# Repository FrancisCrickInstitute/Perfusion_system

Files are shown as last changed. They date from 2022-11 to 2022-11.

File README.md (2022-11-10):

# Perfusion_system

This system is composed by a 3D printed lid for 35 mm petri dishes, two peristaltic pumps and a control board which controls the flow rate of both pumps simultaneously.



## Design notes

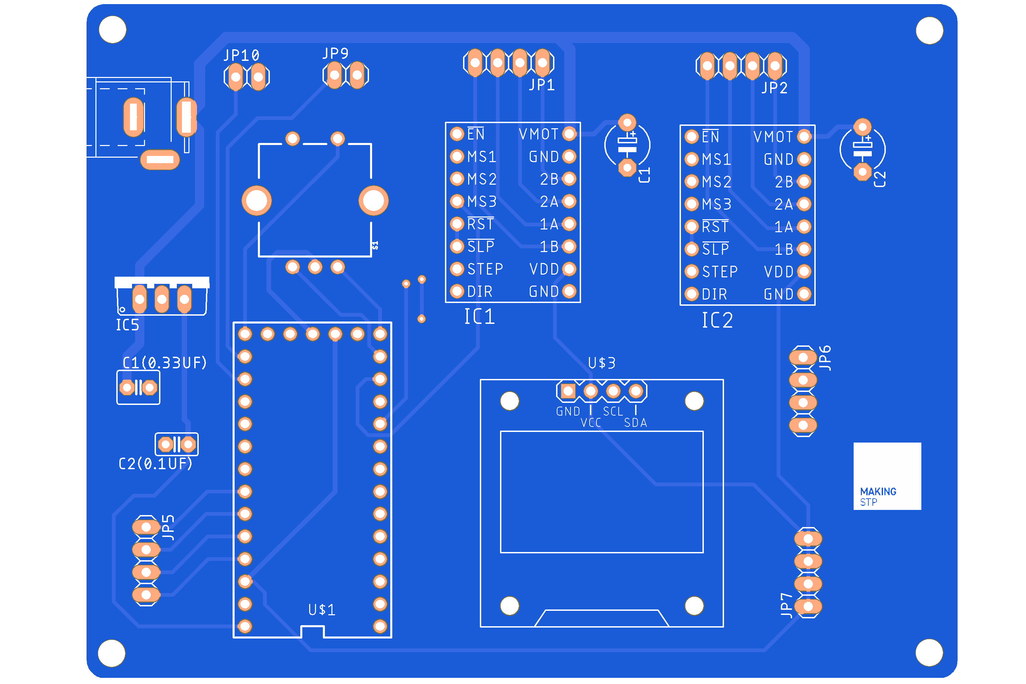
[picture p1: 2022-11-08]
Design files/Electronics/2 stepper board.png

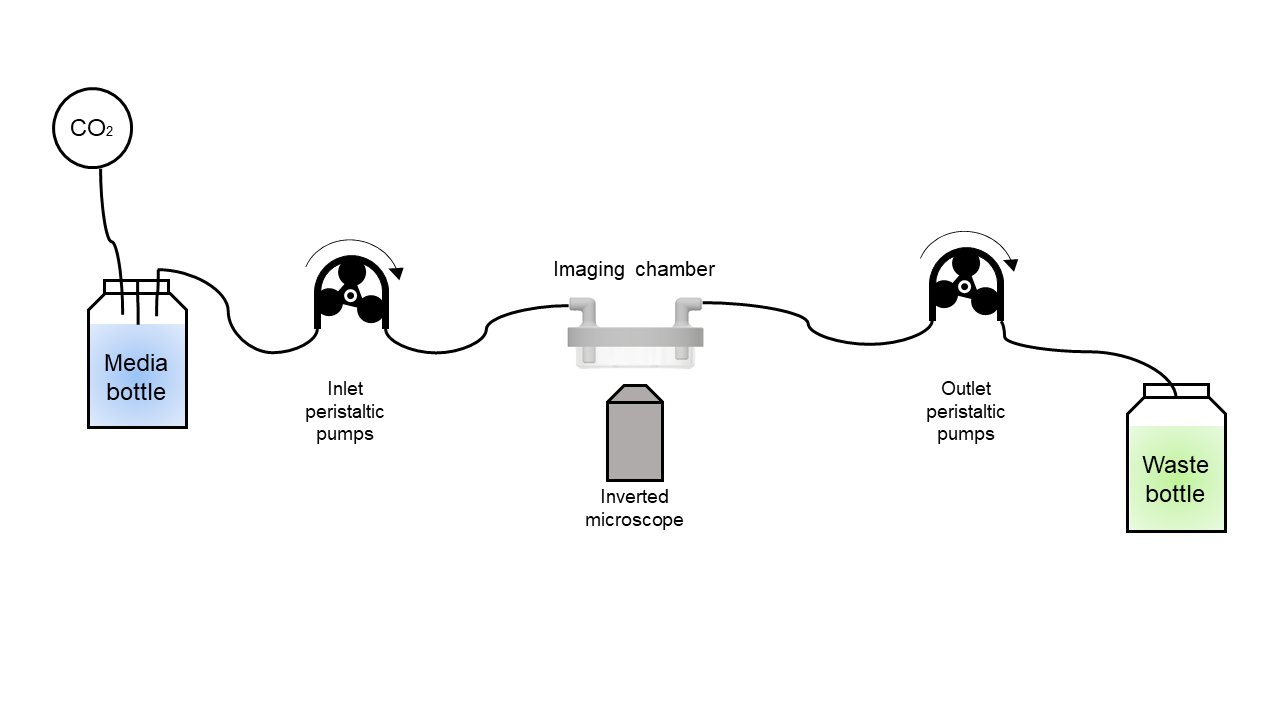
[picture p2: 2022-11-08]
Perfusion system.png

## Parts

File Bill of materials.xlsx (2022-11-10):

Component | Units | Manufacturer Hyperlink embedded) | Unit cost £ | Cost £
Peristaltic pumps | 2 | Amazon (https://www.amazon.co.uk/Elprico-Peristaltic-Pump-12-24V-Micro/dp/B08TLVLJKD) | 36.00 | 72.00
Silicone tubing 2mm ID/ 4mm OD | 1 | RS Components (https://uk.rs-online.com/web/p/flexible-tubes/4189999/)
Teensy 3.2 | 1 | Amazon (https://www.amazon.co.uk/Teensy-3-2-With-Pins/dp/B015QUPO5Y) | 22.39 | 22.39
Barrel jack | 1 | Amazon (https://www.amazon.co.uk/Bottam-Power-Socket-2-1mm-Barrel-Type/dp/B09MQTLXJK?spLa=ZW5jcnlwdGVkUXVhbGlmaWVyPUExMFMxMU8wNUpKUVJ) | 0.10 | 0.10
OLED display | 1 | Amazon (https://www.amazon.co.uk/gp/product/B01L9GC470/ref=ppx_yo_dt_b_search_asin_title?ie=UTF8&th=1) | 5.99 | 5.99
2.54 mm Female pin header | 2 | Amazon (https://www.amazon.co.uk/HALJIA-Header-Connector-2-54mm-StripWires/dp/B06WD34L1H) | 0.50 | 1.00
Screw connectors | 4 | Amazon (https://www.amazon.co.uk/UCTOP-STORE-2-54mm-Terminal-Connector/dp/B01FS4KDN6) | 0.33 | 1.33
Pololu A4988 Stepper Motor Driver Carrier | 2 | Pimoroni (https://shop.pimoroni.com/products/pololu-a4988-stepper-motor-driver-carrier-black-edition?variant=385708716&currency=GBP) | 7.50 | 15.00
5V 1.5A Linear Voltage Regulator - 7805 | 1 | ThePiHut (https://thepihut.com/products/5v-1-5a-linear-voltage-regulator-7805-to-220) | 0.80 | 0.80
330 nF ceramic capacitor | 1 | ThePiHut (https://thepihut.com/products/capacitor-0-33-f-10-pack) | 0.09 | 0.09
100 nF ceramic capacitor | 1 | ThePiHut (https://thepihut.com/products/0-1uf-ceramic-capacitors-10-pack) | 0.17 | 0.17
Rotary encoder | 1 | ThePiHut (https://thepihut.com/products/rotary-encoder-extras) | 3.90 | 3.90
PCB | 1 | Gerber file (JCB PCB) (https://cart.jlcpcb.com/quote?orderType=1&stencilLayer=2&stencilWidth=100&stencilLength=100) | 2.00 | 2.00
12V power supply Barrel jack 2.1mm | 1 | Amazon (https://www.amazon.co.uk/12V-3A-Adapter-Keyboard-Approved/dp/B0B8JX1MZ4) | 12.00 | 2.00
35 mm lid | 2 | 3D printed | 1.00 | 1.00
 |  |  | Total cost | 127.77

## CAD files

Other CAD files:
Design files/Ibidi 35 mm custom dish.ipt

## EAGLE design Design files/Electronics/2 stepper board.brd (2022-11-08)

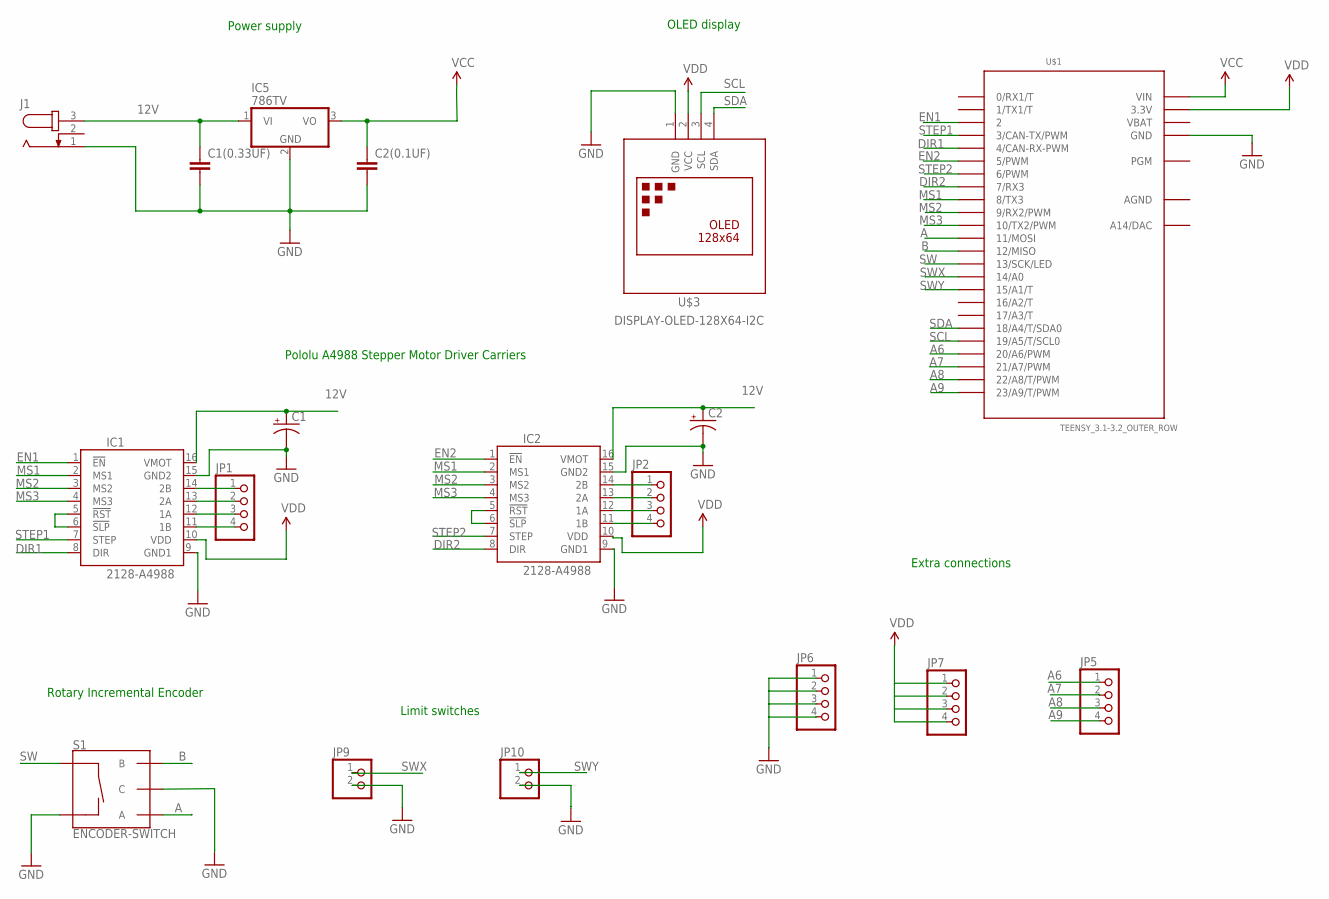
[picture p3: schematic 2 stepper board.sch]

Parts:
C1, C2: CPOL-USE5-5; E5-5
C1(0.33UF): C2.5/4; C2.5-4
C2(0.1UF): C2.5/2; C2.5-2
IC1, IC2: 2128-A4988; A4988
IC5: 786TV; TO220V
J1: JACK-PLUG0; SPC4077
JP1, JP2, JP5, JP6, JP7: PINHD-1X4; 1X04
JP9, JP10: PINHD-1X2; 1X02
S1: ENCODER-SWITCH; ROTARY_ENC_PLAIN
U$1: TEENSY_3.1-3.2_OUTER_ROW; TEENSY_3.0-3.2&LC_OUTER_ROW
U$3: DISPLAY-OLED-128X64-I2C

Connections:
12V: C1.+, C1(0.33UF).1, C2.+, IC1.16 (VMOT), IC2.16 (VMOT), IC5.1 (VI), J1.3
A: S1.A, U$1.11 (11/MOSI)
A6: JP5.1, U$1.20/A6 (20/A6/PWM)
A7: JP5.2, U$1.21/A7 (21/A7/PWM)
A8: JP5.3, U$1.22/A8 (22/A8/T/PWM)
A9: JP5.4, U$1.23/A9 (23/A9/T/PWM)
AGND: U$1.AGND
B: S1.B, U$1.12 (12/MISO)
DIR1: IC1.8 (DIR), U$1.4 (4/CAN-RX-PWM)
DIR2: IC2.8 (DIR), U$1.7 (7/RX3)
EN1: IC1.1 (!EN), U$1.2
EN2: IC2.1 (!EN), U$1.5 (5/PWM)
GND: C1.-, C1(0.33UF).2, C2.-, C2(0.1UF).2, IC1.9 (GND1), IC1.15 (GND2), IC2.9 (GND1), IC2.15 (GND2), IC5.2 (GND), J1.1, JP6.1, JP6.2, JP6.3, JP6.4, JP9.2, JP10.2, S1.C, S1.SW-, U$1.GND, U$1.GND1 (GND), U$3.1 (GND)
MS1: IC1.2 (MS1), IC2.2 (MS1), U$1.8 (8/TX3)
MS2: IC1.3 (MS2), IC2.3 (MS2), U$1.9 (9/RX2/PWM)
MS3: IC1.4 (MS3), IC2.4 (MS3), U$1.10 (10/TX2/PWM)
unnamed: IC1.14 (2B), JP1.1
unnamed: IC1.13 (2A), JP1.2
unnamed: IC1.12 (1A), JP1.3
unnamed: IC1.11 (1B), JP1.4
unnamed: IC2.14 (2B), JP2.1
unnamed: IC2.13 (2A), JP2.2
unnamed: IC2.12 (1A), JP2.3
unnamed: IC2.11 (1B), JP2.4
unnamed: IC2.5 (!RST), IC2.6 (!SLP)
unnamed: IC1.5 (!RST), IC1.6 (!SLP)
SCL: U$1.19/A5 (19/A5/T/SCL0), U$3.3 (SCL)
SDA: U$1.18/A4 (18/A4/T/SDA0), U$3.4 (SDA)
STEP1: IC1.7 (STEP), U$1.3 (3/CAN-TX/PWM)
STEP2: IC2.7 (STEP), U$1.6 (6/PWM)
SW: S1.SW+, U$1.13 (13/SCK/LED)
SWX: JP9.1, U$1.14/A0
SWY: JP10.1, U$1.15/A1 (15/A1/T)
VBAT: U$1.VBAT
VCC: C2(0.1UF).1, IC5.3 (VO), U$1.VIN
VDD: IC1.10 (VDD), IC2.10 (VDD), JP7.1, JP7.2, JP7.3, JP7.4, U$1.3.3V, U$1.3.3V1 (3.3V), U$3.2 (VCC)

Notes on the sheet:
Pololu A4988 Stepper Motor Driver Carriers
OLED display
Power supply
Rotary Incremental Encoder
Extra connections
Limit switches

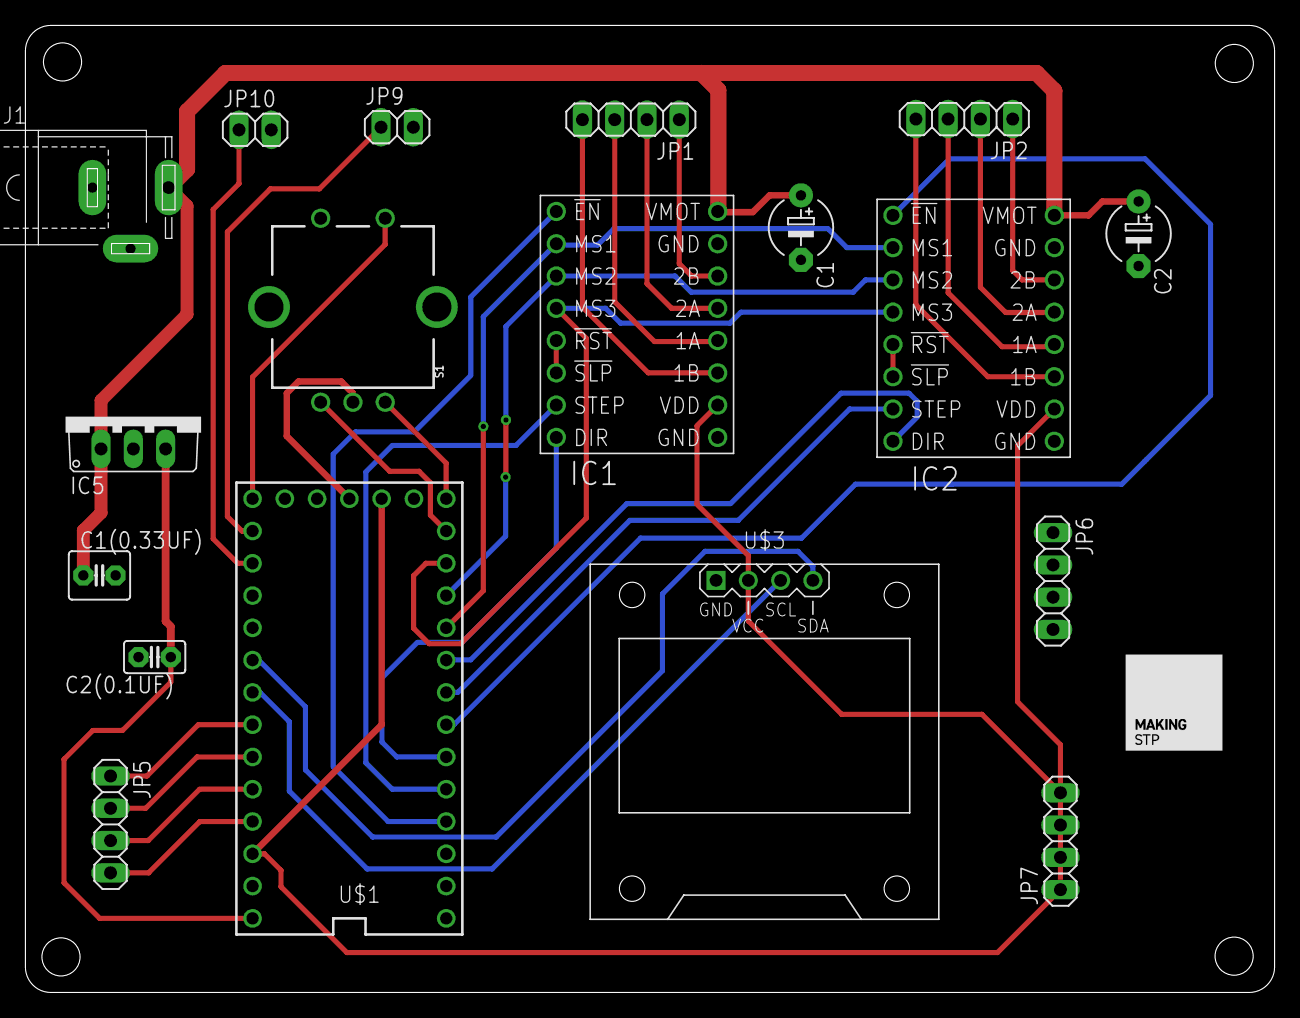
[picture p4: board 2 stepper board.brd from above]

Board: 2 copper layers, 98.3 x 76.1 mm, 18 parts (0 on the bottom side), 34 nets.

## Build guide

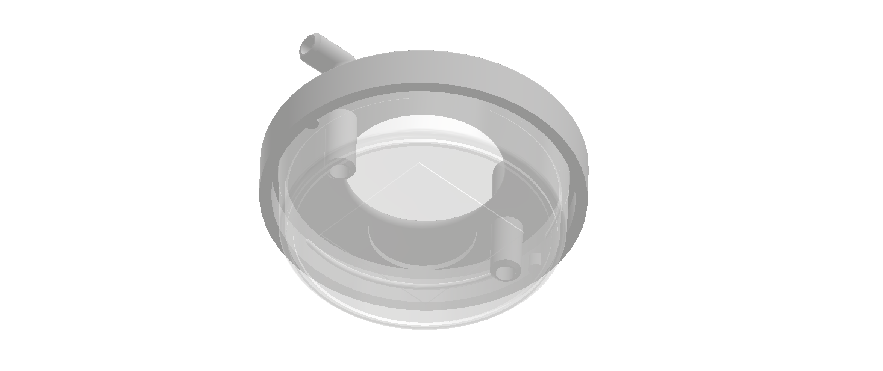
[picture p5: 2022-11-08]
AssemblyPerti dish4.png

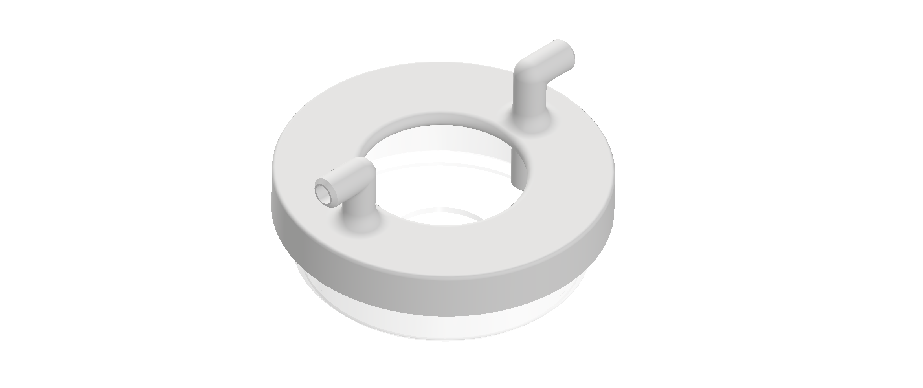
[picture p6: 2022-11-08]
AssemblyPerti dish3.png

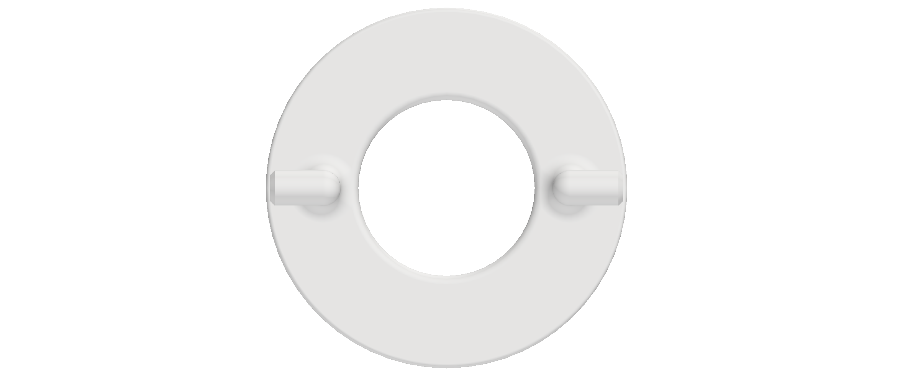
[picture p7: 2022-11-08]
AssemblyPerti dish top.png

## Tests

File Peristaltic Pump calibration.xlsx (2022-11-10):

Speed(steps/s) | Time (s) | Volume (mL) | Flow (mL/s) | Flow (mL/min)
150 | 600 | 5 | 0.01 | 0.5
350 | 600 | 12.5 | 0.02 | 1.25
500 | 600 | 18 | 0.03 | 1.8
1000 | 420 | 26 | 0.06 | 3.714285714

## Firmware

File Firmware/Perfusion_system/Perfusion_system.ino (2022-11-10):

#include "TeensyStep.h"
#include <Encoder.h>
#include <Wire.h>
#include <Adafruit_GFX.h>
#include <Adafruit_SSD1306.h>
#include <Bounce.h>

Encoder knob(11, 12);
const int encoder_SW = 13;
Bounce pushbutton = Bounce(encoder_SW, 10);  // 10 ms debounce
bool state = 0;

Stepper pump(3, 4);       // STEP pin: 7, DIR pin: 6  // The stepper class encapsulates the physical properties of a stepper motor like pin numbers of the STEP and DIR signals, speed and acceleration of the motor.
Stepper pump2(6, 7); 

//StepControl step_controller;    // The StepControl class is used to synchronously move up to 10 motors to their target positions.
RotateControl rotate_controller; // The RotateControl class is used to synchronously rotate up to 10 motors.
RotateControl rotate_controller2; // The RotateControl class is used to synchronously rotate up to 10 motors.
int speed_ = 0;

float flow_rate;
int steps_s;

#define SCREEN_WIDTH 128 // OLED display width, in pixels
#define SCREEN_HEIGHT 64 // OLED display height, in pixels

// Declaration for an SSD1306 display connected to I2C (SDA, SCL pins)
#define OLED_RESET     -1 // Reset pin # (or -1 if sharing Arduino reset pin)

Adafruit_SSD1306 display(SCREEN_WIDTH, SCREEN_HEIGHT, &Wire, OLED_RESET);

const int MS1 = 8;
const int MS2 = 9;
const int MS3 = 10;
const int Enable = 2;
const int Enable2 = 5;

//Direction
bool dir = false;

void setup()
{
  pinMode(MS1, OUTPUT);    // set the MS1, MS2, MS3 and Enable as an outputs
  pinMode(MS2, OUTPUT);
  pinMode(MS3, OUTPUT);
  pinMode(Enable, OUTPUT);

  digitalWrite(MS1, HIGH); // sets the digital pin MS1, MS2, MS3 to HIGH
  digitalWrite(MS2, HIGH);
  digitalWrite(MS3, HIGH);
  //digitalWrite(Enable, HIGH); // set the enable to HIGH
  //digitalWrite(Enable2, HIGH); // set the enable to HIGH
  
  // Set the motor max acceleration
  pump.setAcceleration(500)   // stp/s^2
      .setInverseRotation(true);

  pump2.setAcceleration(500)   // stp/s^2
      .setInverseRotation(true);

  pinMode(encoder_SW, INPUT_PULLUP);
  
  Serial.begin(115200);
  
  display.begin(SSD1306_SWITCHCAPVCC, 0x3C);
  delay(1000); 
  display.clearDisplay();

  digitalWrite(Enable, LOW);
  digitalWrite(Enable2, LOW);

}

void loop() 
{ 
  speed_ = abs(knob.read()/4*10);
  flow_rate = speed_*0.0038;

  pump.setMaxSpeed(speed_);
  pump2.setMaxSpeed(speed_);

  //Serial.println(speed_);
  rotate_controller.overrideSpeed(speed_);
  rotate_controller2.overrideSpeed(speed_);
  
  rotate_controller.rotateAsync(pump);
  rotate_controller2.rotateAsync(pump2);

  OLED_display();

}


void OLED_display()
{   
    display.clearDisplay();
    display.setTextColor(WHITE);        // Draw white text
    display.setCursor(0, 0);
    display.setTextSize(1);
    display.print(F("Perfusion system"));
    display.setTextSize(1);
    display.println();
    display.println();
//    display.print(F("Flow rate selected:"));
//    display.println();
//    display.setTextSize(1);
//    display.print(flow_rate);
//    display.setTextSize(1);
//    display.println  (F(" mL/min"));
//    display.print(F("Flow rate dispensed:"));
//    display.println();
//    display.print(rotate_controller.getCurrentSpeed()*linear_resolution*60); 
//    display.println  (F(" uL/min"));
//    display.print(F("Controller 1:"));
//    display.println();
//    display.print(rotate_controller.getCurrentSpeed()); 
//    display.println  (F(" Steps"));
//    display.setTextSize(1);
//    display.print(F("Controller 2:"));
//    display.println();
//    display.print(rotate_controller2.getCurrentSpeed()); 
//    display.println  (F(" Steps"));
    display.print(F("Flow rate:"));
    display.print(rotate_controller.getCurrentSpeed()*0.0038);
    display.setTextSize(1);
    display.println(F(" mL"));
    display.display(); 
}

void read_pushbutton()
{
    if (pushbutton.update()) 
    {
      if (pushbutton.fallingEdge()) 
      {
        state = !state;
      }
    } 
}

void pushbutton_activated()
{
  read_pushbutton();
  
  speed_ = abs(knob.read()/2*10);

  flow_rate = speed_*0.0038;

  OLED_display();
 
  digitalWrite(Enable, HIGH);
  digitalWrite(Enable2, HIGH);
  
  rotate_controller.stop();
  rotate_controller2.stop();
  
  while (state == HIGH)
  {
    read_pushbutton();
        
    digitalWrite(Enable, LOW);
    digitalWrite(Enable2, LOW);
    
    speed_ = abs(knob.read()/2*10);
    flow_rate = speed_*0.0038;
  
    pump.setMaxSpeed(speed_);
    pump2.setMaxSpeed(speed_);
    
    rotate_controller.rotateAsync(pump);
    rotate_controller2.rotateAsync(pump2);
  
    OLED_display();
 }
}

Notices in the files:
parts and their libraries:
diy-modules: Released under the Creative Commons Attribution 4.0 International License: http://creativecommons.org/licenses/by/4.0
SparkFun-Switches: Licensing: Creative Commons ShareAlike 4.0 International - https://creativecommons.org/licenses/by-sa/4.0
